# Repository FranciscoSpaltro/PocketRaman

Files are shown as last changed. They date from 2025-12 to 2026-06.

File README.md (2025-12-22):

# PocketRaman
Low-cost portable Raman spectrometer prototype developed at SUPSI. Based on Raspberry Pi 4 and STM32F469I-DISCO, using a TCD1304 linear CCD with ADC and DMA-based acquisition. Includes custom 3D-printed mechanical parts to reuse optical mounting components and reduce cost.

## Status

This project implements a first working pipeline for CCD readout using:
- Timer-driven ADC sampling with DMA
- UART DMA streaming to host
- Python-based real-time visualization

Data acquisition and transmission are functional.
Frame synchronization relative to ICG/SH is currently under refinement,
which may cause horizontal drift in the displayed signal.

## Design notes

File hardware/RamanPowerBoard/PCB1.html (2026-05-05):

Altium customize

# Board Information Report

Date: | | 5/5/2026
Time: | | 11:02:39
Elapsed Time: | | 00:00:00
Filename: | | C:\Users\francisco.spaltro\OneDrive - SUPSI\Desktop\PocketRaman\hardware\RamanPowerBoard\PCB1.PcbDoc

## Contents

Contents

Routing

Routing Information

## Routing

Routing Information
Routing completion | 100,00%
Connections | 118
Connections routed | 118
Connections remaining | 0

Back to top

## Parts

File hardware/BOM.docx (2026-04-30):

BOM – PCB A

QTY | NAME | DESCRIPTION | SEL
6 | STACKPOLE RMCF0805ZT0R00TR-ND | RESISTOR 0 OHM | SEL.000028 (4400 PZ)
3 | YAGEO 311-100CRTR-ND (RC0805FR-07100RL) | RESISTOR 100 OHM | SEL.000034 (4400 PZ)
1 | STACKPOLE RMCF0805FT150RTR-ND | RESISTOR 150 OHM | SEL.000038 (4400 PZ)
1 | YAGEO 311-220FRTR-ND (RC1206FR-07220RL) | RESISTOR 220 OHM | SEL.001229 (20 PZ)
3 | STACKPOLE RMCF0805FT1K00 | RESISTOR 1 KOHM | SEL.000049 (4400 PZ)
9 | YAGEO 311-10KARTR-ND (RC0805JR-0710KL) | RESISTOR 10 KOHM | SEL.000062 (4400 PZ)
2 | Kemet C0805C100J5GACTU | CAPACITOR 10 pF | SEL.000911 (984 PZ)
1 | Kemet C0805C101J5GACTU | CAPACITOR 100 pF | SEL.000857 (990 PZ)
19 | Kemet C0805C104K3RAC7800 | CAPACITOR 100 nF | SEL.000087 (1000 PZ)
4 | Samsung CL21B475KOFNNNE | CAPACITOR 4.7 uF | SEL.001701 (4 PZ)
1 | Yageo CC0805KKX7R7BB105 | CAPACITOR 1 uF | SEL.000086 (1000 PZ)
5 | Samsung CL21B106KOQNNNE | CAPACITOR 10 uF | SEL.000690 (29 PZ)
2 | Kyocera AVX F381A106MMA | CAPACITOR 10 uF | SEL.001502 (6 PZ)
1 | Kyocera AVX F951A226MPAAQ2 | CAPACITOR 22 uF | SEL.000755 (10 PZ)
2 | BAS40-7-F | DIODE | SEL.000247 (72 PZ)
1 | ONSEMI MBRA340T3G | DIODE SCHOTTKY 40V 3A SMA | SEL.001040 (16 PZ)
1 | ONSEMI BC846BLT1G | TRANS NPN 65V 0.1A SOT23-3 | SEL.001790 (21 PZ)
1 | DIOTEC BC857B-AQ | TRANS PNP 45V 0.1A SOT23-3 | SEL.000739 (8 PZ)
2 | MMZ1608B601CTAH0 | INDUCTOR; SMT (0603); FERRITE-BEAD; 600; TOL=+/-25%; 0.5A; -55 DEGC TO +125 DEGC | SEL.001136 (163 PZ)
1 | NCV1117ST33T3G | Linear Voltage Regulator IC Positive Fixed 1 Output 1A SOT-223 | SEL.000321 (5 PZ)
1 | NCV1117STAT3G | IC REG LINEAR POS ADJ 1A SOT-223 | NOT AVAILABLE
1 | CG04874-8M | 8 MHz ±20ppm Crystal 8pF 500 Ohms 2-SMD, No Lead | SEL.000471 (1 PZ)
1 | MCP6001UT-E/OT | Microchip MCP6001UT-E/OT Op Amp, 1MHz Rail-Rail, 1.8 - 6 V, 5-Pin SOT-23 | Microchip Technology Inc. MCP6001UT-E/OT | SEL.000435 (10 PZ)
1 | STM32F446RCT6TR | ARM® Cortex®-M4 STM32F4 Microcontroller IC 32-Bit Single-Core 180MHz 256KB (256K x 8) FLASH 64-LQFP (10x10) | SEL.001604 (1 PZ)
1 | LED-LTST-C190KRKT | Red 631nm LED Indication - Discrete 2V 0603 (1608 Metric) | SEL.000817 (254 PZ)
2 | OMRON SW1020TR-ND | Switch Tactile N.O. SPST Round Button Gull Wing 0.05A 12VDC 1.5N SMD Embossed T/R | SEL.000613 (21 PZ)
1 | MCP9808T-E/MC | TEMPERATURE SENSOR | -
1 | TCD1304DG8ZAW | LINEAR CCD DETECTOR | -
1 | AMPHENOL ICC (FCI)10118194-0001LF | Micro USB, Input Output Connectors, B TYPE RECEPTACLE with flange | SEL.000758 (47 PZ)
1 | USBLC6-4SC6 | VERY LOW CAPACITANCE ESD PROTECTION | SEL.000267 (25 PZ)
1 | SILICON LABS 336-1160-5-ND (CP2102-GM) | USB Bridge, USB to UART USB 2.0 UART Interface 28-QFN (5x5) | SEL.000346 (6 PZ)
3 | Generic 40 mils drill size, 100 mils step. TOTAL: 36 PIN | Pin header x3
1 | | Pin header x4
1 | | Pin header x5
3 | | Pin header x6
1 | HARWIN M20-7861546 | PIN SOCKET SMD 2x15 (CCD SENSOR) | NOT AVAILABLE
1 | PHOENIX 1706207 | TERM BLOCK HDR 2POS 2.54MM | NOT AVAILABLE
1 | PHOENIX 1821465 | TERM BLOCK HDR 9POS 2.54MM | NOT AVAILABLE

BOM – PCB B

QTY | NAME | DESCRIPTION | SEL
7 | STACKPOLE RMCF0805ZT0R00TR-ND | RESISTOR 0 OHM | SEL.000028 (4400 PZ)
1 | STACKPOLE RMCF0805FT10R0TR-ND | RESISTOR 10 OHM | SEL.000031 (4400 PZ)
6 | YAGEO 311-10KARTR-ND (RC0805JR-0710KL) | RESISTOR 10 KOHM | SEL.000062 (4400 PZ)
1 | Kemet C0805C101J5GACTU | CAPACITOR 100 pF | SEL.000857 (990 PZ)
7 | Kemet C0805C104K3RAC7800 | CAPACITOR 100 nF | SEL.000087 (1000 PZ)
1 | Taiyo Yuden 587-2994-2-ND (UMK316AB7475KL-T) | CAPACITOR 4.7 uF | SEL.000799 (500 PZ)
1 | Samsung 1276-1075-2-ND (CL31A106KAHNNNE) | CAPACITOR 10 uF | SEL.001145 (990 PZ)
4 | Panasonic PCE3836TR-ND (EEE-FK1V101XP) | CAPACITOR 100 uF | SEL.001144 (48 PZ)
1 | ONSEMI FSV15150V | DIODE SCHOTTKY 150V 15A TO2773 | SEL.000715 (6 PZ)
2 | AO 785-1106-2-ND (AOD417) | P-Channel 30V 25A, 2.5W Ta, 50W Tc Surface Mount TO-252, D-Pak | SEL.001625 (8 PZ)
1 | MICROCHIP TC4420COA713TR-ND | MOSFET Power Driver 6A,4.5 to 18V, Non-Inverting,8-Pin SOIC | Microchip Technology Inc. TC4420COA | SEL.001374 (1 PZ)
1 | WÜRTH 732-11711-ND (74437529203220) | FIXED IND 22UH 23.9A 4.9MOHM SMD | SEL.001103 (3 PZ)
2 | POLOLU A4988 | Stepper Motor Driver Carrier | -
1 | PHOENIX 1706207 | TERM BLOCK HDR 2POS 2.54MM | NOT AVAILABLE
1 | PHOENIX 1821465 | TERM BLOCK HDR 9POS 2.54MM | NOT AVAILABLE
2 | MOLEX WM11252-ND (436500402) | Connector Header Through Hole, Right Angle 4 position 0.118 (3.00mm) | SEL.001696 (3 PZ)
4/2 | PIN SOCKET | 1 x 8 POS / 2 x 8 POS

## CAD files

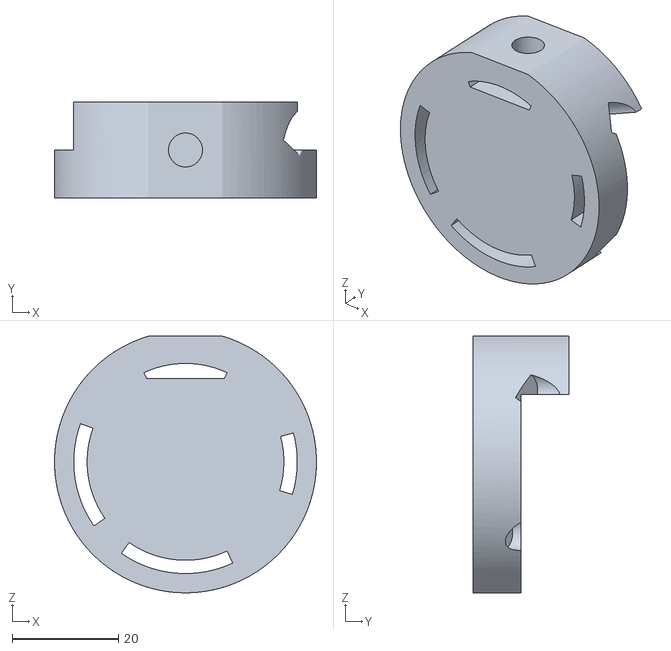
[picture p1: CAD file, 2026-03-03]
mechanical/13_grating-cage.stl
49.2 x 18.0 x 48.2

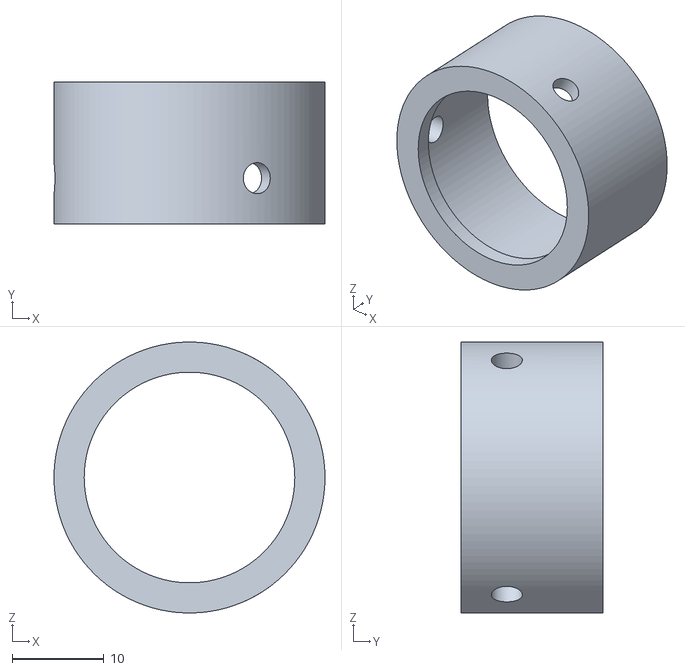
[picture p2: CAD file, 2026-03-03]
mechanical/11_25-4-lens-adapter.stl
29.6 x 15.5 x 29.6

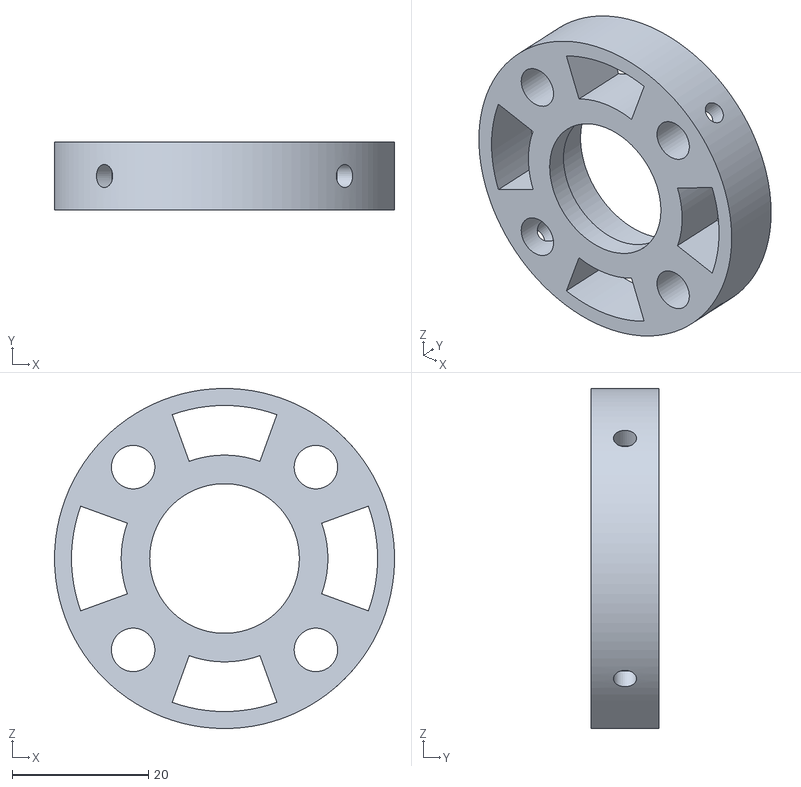
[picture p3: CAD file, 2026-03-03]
mechanical/06_filter-cage.stl
50.0 x 10.0 x 50.0

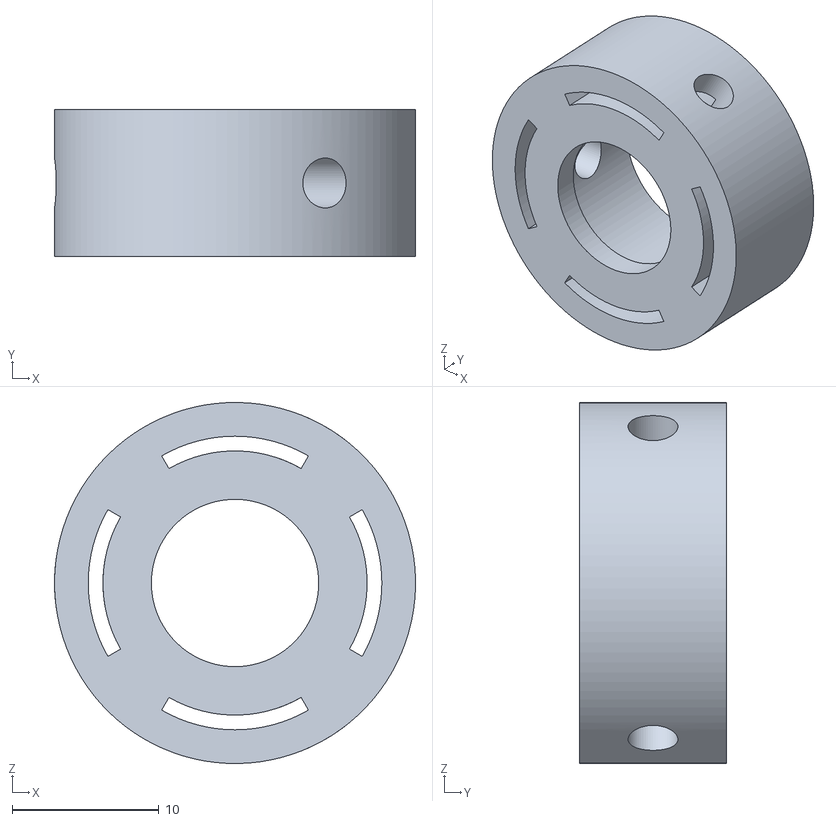
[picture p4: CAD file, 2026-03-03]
mechanical/02_12-7-lens-adapter-a.stl
24.6 x 10.0 x 24.6

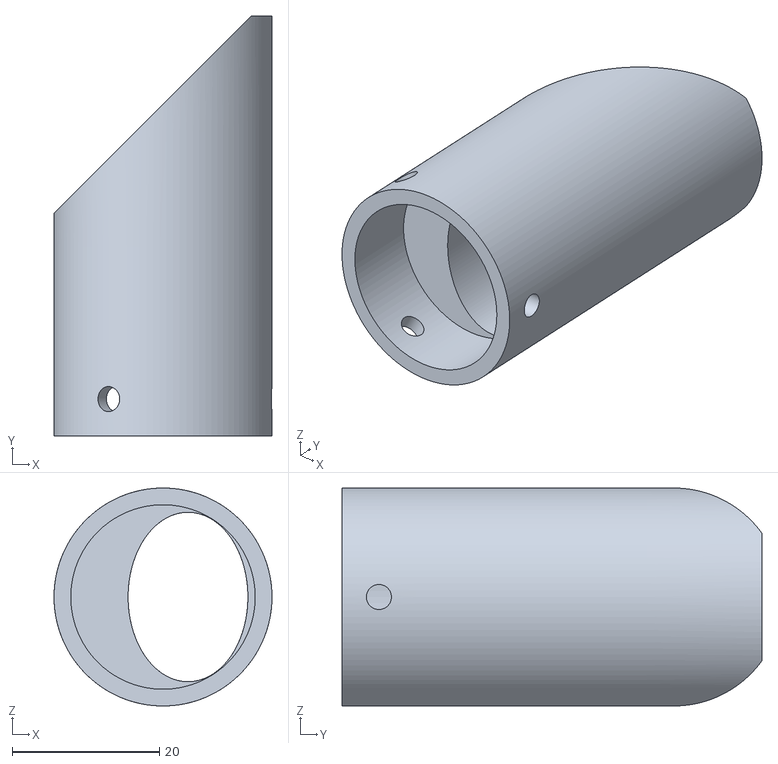
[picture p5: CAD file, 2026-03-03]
mechanical/04_dichroic-adapter.stl
29.6 x 57.0 x 29.6

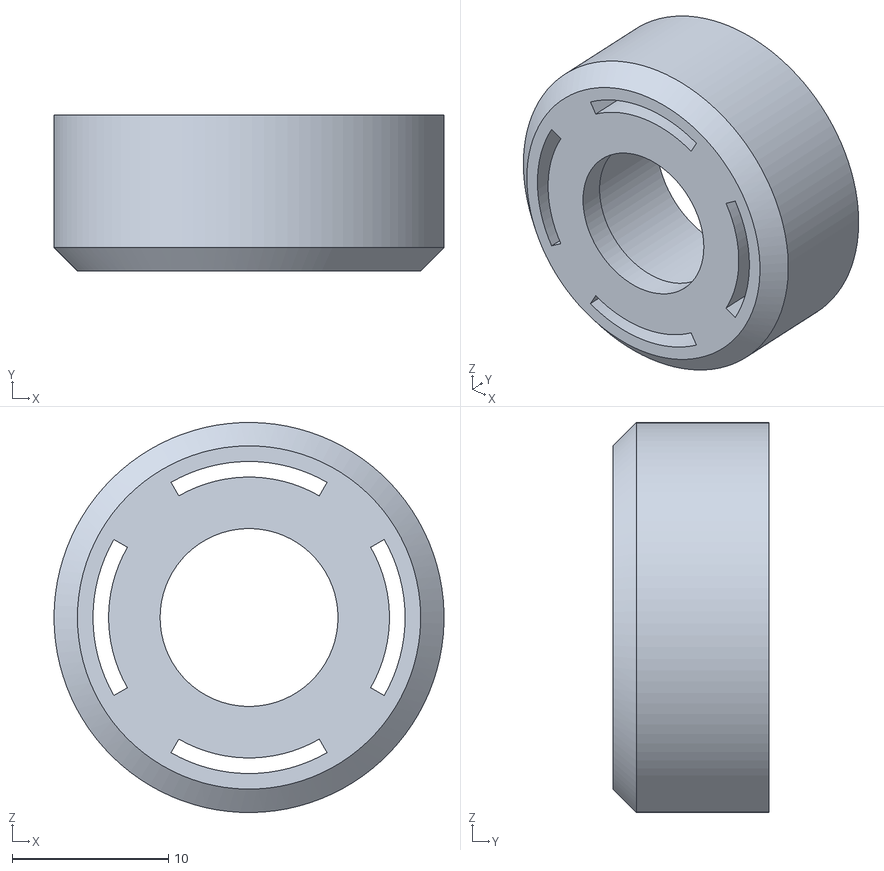
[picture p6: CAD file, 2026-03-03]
mechanical/08_12-7-lens-adapter-b.stl
25.0 x 10.0 x 25.0

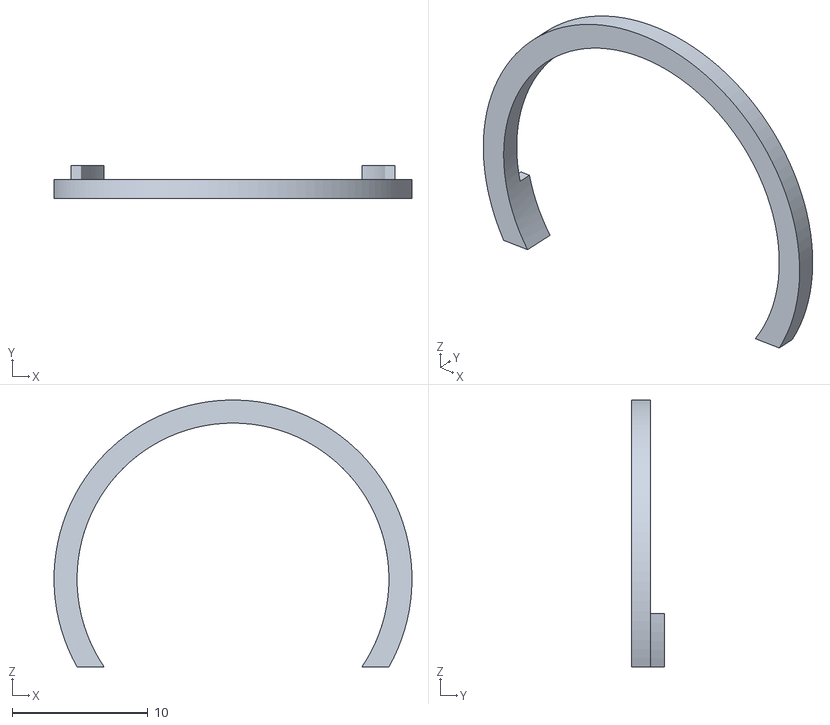
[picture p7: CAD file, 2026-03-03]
mechanical/05_dichroic-stop.stl
26.4 x 2.40 x 19.7

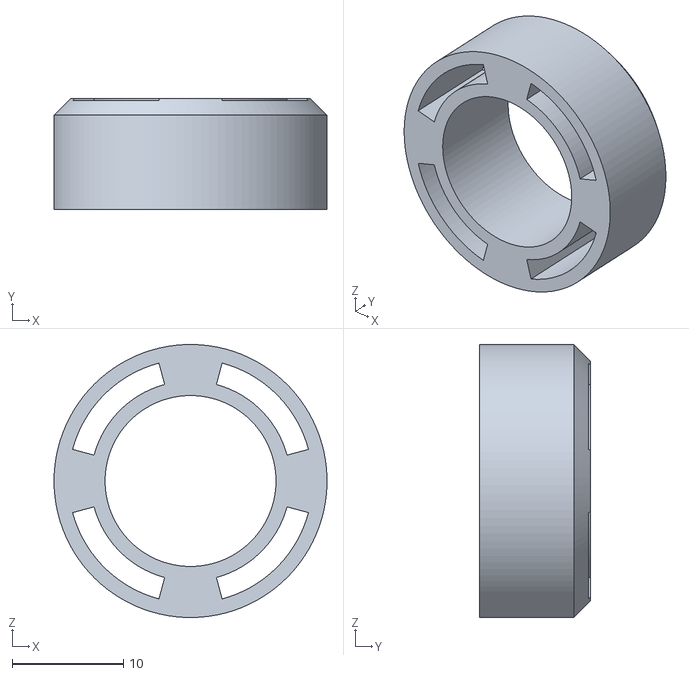
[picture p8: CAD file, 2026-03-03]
mechanical/01_laser-adapter.stl
24.6 x 10.0 x 24.6

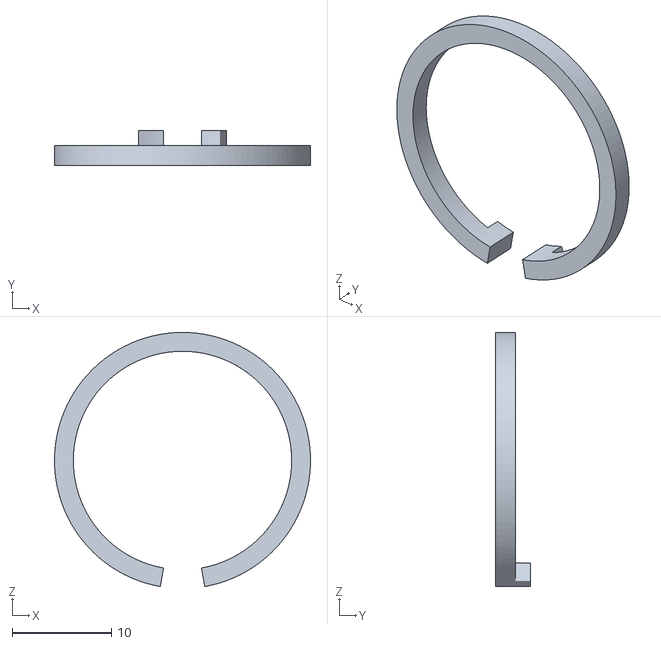
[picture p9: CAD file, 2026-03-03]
mechanical/07_filter-stop.stl
25.8 x 3.50 x 25.6

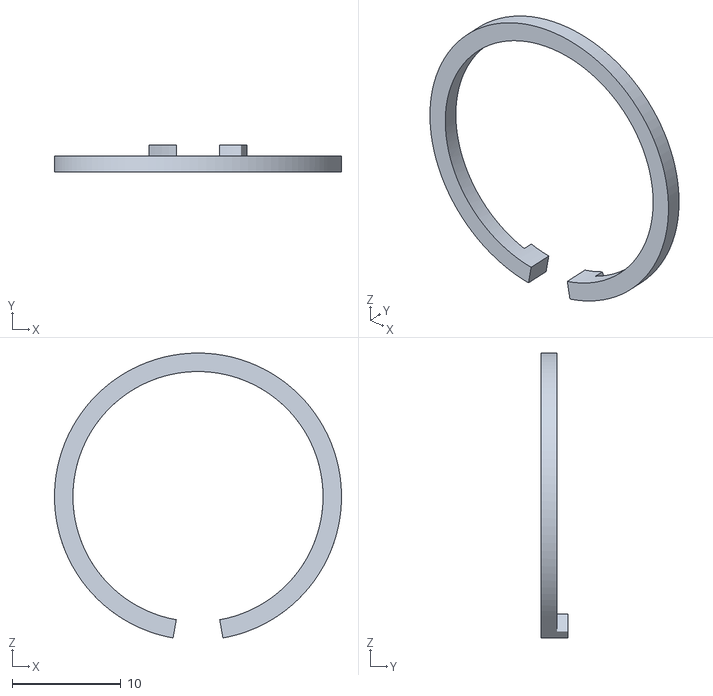
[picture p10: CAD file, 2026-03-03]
mechanical/12_25-4-lens-stop.stl
26.4 x 2.50 x 26.2

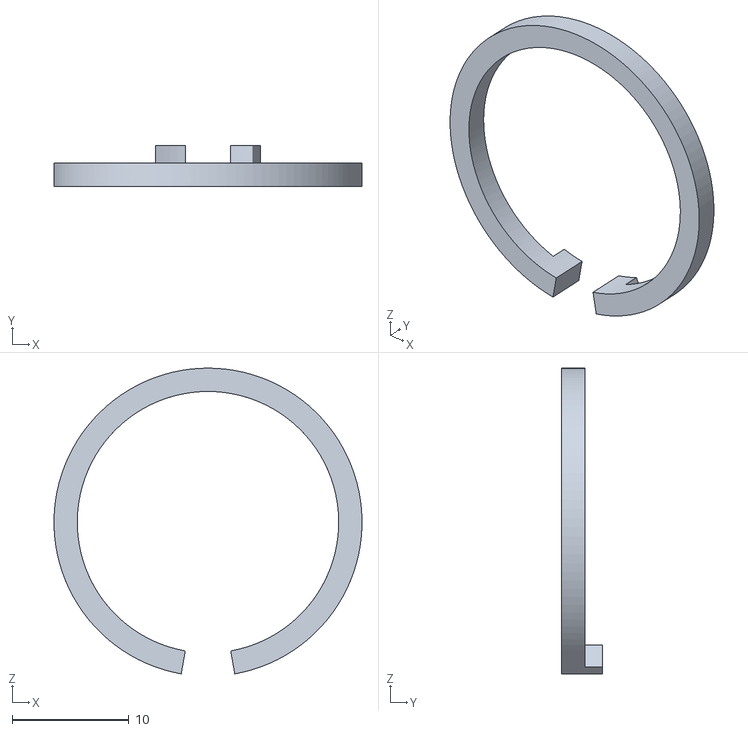
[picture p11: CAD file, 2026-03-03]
mechanical/10_slit-stop.stl
26.4 x 3.50 x 26.2

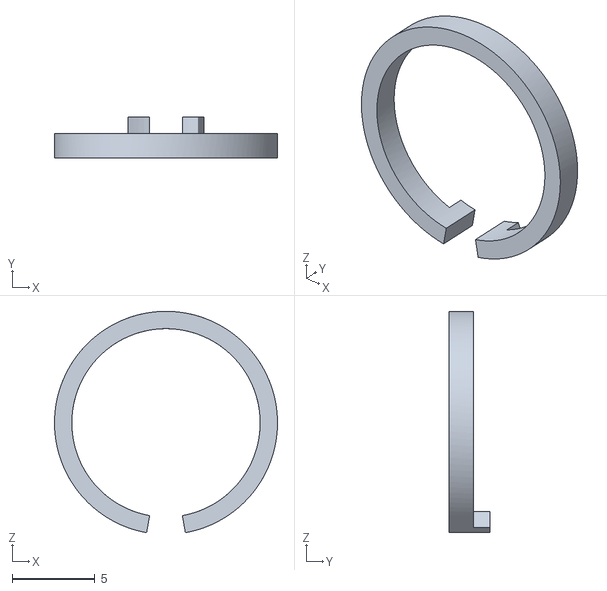
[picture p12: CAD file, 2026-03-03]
mechanical/03_12-7-lens-stop.stl
13.5 x 2.50 x 13.4

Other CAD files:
mechanical/09_slit-adapter.stl

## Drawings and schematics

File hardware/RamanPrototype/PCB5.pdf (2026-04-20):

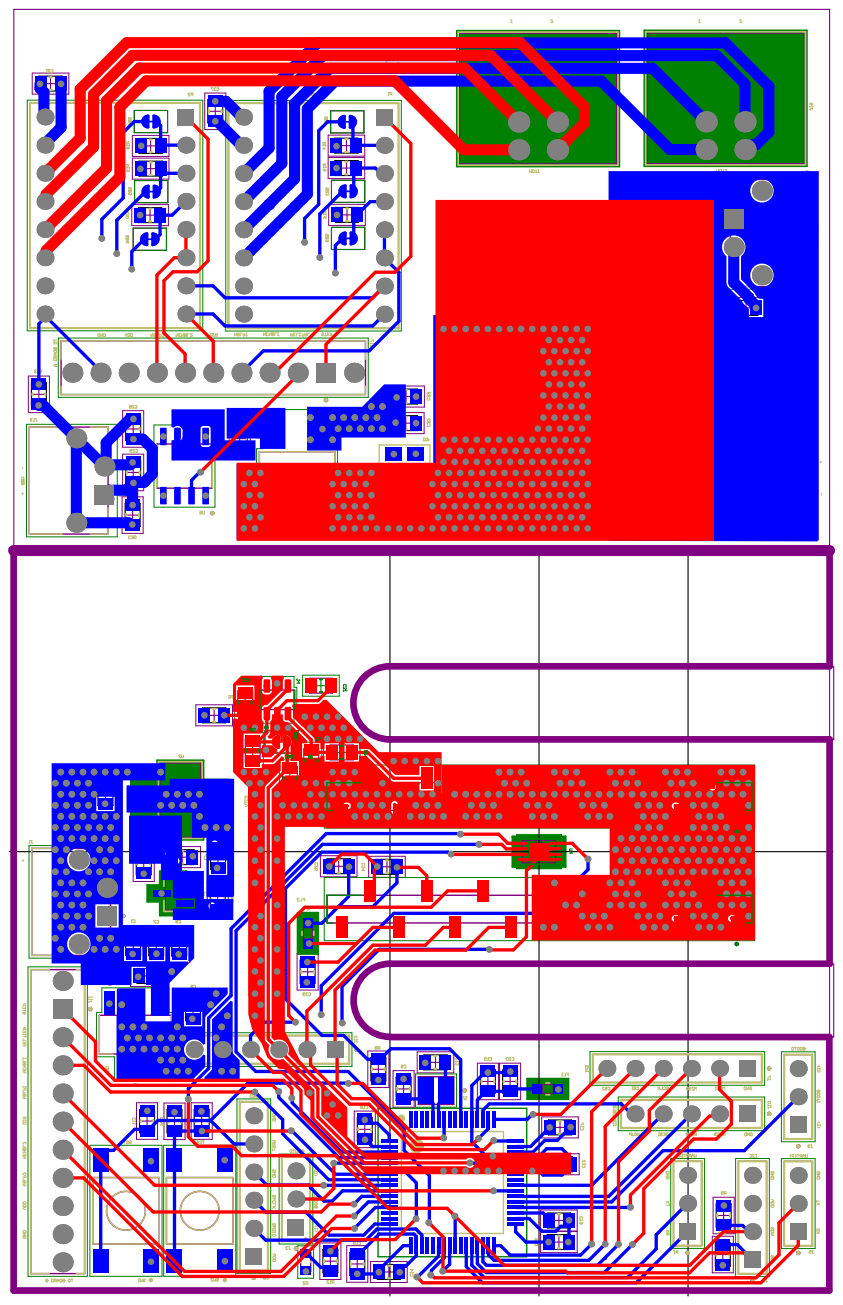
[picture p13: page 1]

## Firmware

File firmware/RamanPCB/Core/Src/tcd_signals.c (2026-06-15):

#include <tcd_signals.h>
#include <tcd_variables.h>

extern TIM_HandleTypeDef htim1;
extern TIM_HandleTypeDef htim3;
extern TIM_HandleTypeDef htim5;
extern ADC_HandleTypeDef hadc1;
extern volatile uint8_t send_now;
//extern volatile uint8_t is_flushing;
extern volatile uint32_t n_accum;
extern volatile uint32_t n_skip_counter;

volatile uint8_t adc_busy = 0;
volatile uint8_t can_save = 1;
volatile uint32_t skip_counter = 0;

volatile uint16_t adc_buffer[CCD_PIXELS];
volatile uint32_t accum_buffer[CCD_PIXELS] = {0};
volatile uint16_t frame[CCD_PIXELS];

volatile int n = 0;
volatile int real_SH_EDGES = 0;
uint32_t sh_ccr[SH_EDGES_MAX];
volatile int acumulaciones = 0;

const uint32_t TS0_tics = 1;
const uint32_t TS1_tics = 2;
const uint32_t TS2_tics = 10;

uint32_t TS3_tics = 0;
uint32_t TS4_tics = 0;
uint32_t TS5_tics = 0;
uint32_t TS6_tics = 0;


/**
 * @brief Calculo de los tiempos de cada etapa de la integración y de la cantidad de overhead necesaria para cumplir con el tiempo de lectura
 *
 * @param[in]	t_int_us	Nuevo tiempo de integración en microsegundos
 * @return		void
 *
 * @post Se configuraron los nuevos valores de TS3_tics, TS4_tics, TS5_tics, TS6_tics y n
 * Deben recalcularse las tablas CCR de SH e ICG
 */
void calculate_times(uint32_t t_int_us){
    // fM = 2 MHz -> 1 us = 2 tics
	const uint16_t tics_por_microsegundo = 2;			// [REVISAR] -> hacerlo portable
    uint32_t t_int_tics = 0;

    if(t_int_us < T_INT_MIN_US)
        t_int_tics = T_INT_MIN_US * tics_por_microsegundo;
    /*else if(t_int_us > T_INT_MAX_US)
    	t_int_tics = T_INT_MAX_US * tics_por_microsegundo;*/
    else
        t_int_tics = t_int_us * tics_por_microsegundo;

    /*
     * MODELO: desde el momento que baja ICG:
     * S0: desde la bajada de ICG hasta la subida de SH -> (100, 500, 1000) ns
     * S1: tiempo en ON de SH dentro del tiempo en OFF de ICG -> (1000, -, -) ns [si se necesita padding se puede modificar este -> hay que actualizar ICG]
     * S2: desde la bajada de SH hasta la subida de ICG -> (1000, 5000, - ) ns
     * S3: desde la subida de ICG hasta la subida de SH -> t_int - S1 - S2
     * S4: tiempo en ON de SH -> TS1 (sin padding)
     * S5: tiempo en OFF de SH -> t_int - S4
     * S6: desde la bajada de SH hasta la bajada de ICG -> TS5 - TS0
     */
    TS3_tics = t_int_tics - TS1_tics - TS2_tics;
    TS4_tics = TS1_tics;
    TS5_tics = t_int_tics - TS4_tics;
    TS6_tics = TS5_tics - TS0_tics;

    const uint32_t t_readout_tics = 7400 * tics_por_microsegundo;

    // Cálculo de 'n' (Número de pulsos de limpieza durante el readout)
    /*
     * TS3 + n * (TS4 + TS5) + TS4 + TS6 >= t_readout
     * n >= (t_readout - TS3 - TS4 - TS6) / (TS4 + TS5) = (t_readout - TS3 - TS4 - TS6) / t_int
     */

    uint32_t overhead = TS0_tics + TS1_tics + TS2_tics + TS3_tics + TS4_tics + TS6_tics;	// Tiempo sin contar los ciclos TS4-TS5

    if (t_readout_tics + t_int_tics > overhead) {
         n = (t_readout_tics - TS3_tics - TS4_tics - TS6_tics + t_int_tics - 1) / t_int_tics;
    } else {
         n = 0;
    }

}

/**
 * @brief Actualización de la tabla de valores CCR para SH
 *
 * @post Se actualizaron los valores del vector sh_ccr
 */
void build_SH_table(void)
{
	// Se arma un vector local con todos los tiempos en base al 'n' actualizado
	static uint32_t sh_dt[SH_EDGES_MAX];

	sh_dt[0] = TS0_tics;
	sh_dt[1] = TS1_tics;
	sh_dt[2] = TS2_tics + TS3_tics;

	for(int i = 0; i < n; i++){
		sh_dt[3 + 2 * i] = TS4_tics;
		sh_dt[3 + 2 * i + 1] = TS5_tics;
	}

	sh_dt[2 + 2 * n + 1] = TS4_tics;

	// De S0 a S0 hay 4 flancos (extremos de S1 y del último S4) más 2*n de cada S4 que se repite
	real_SH_EDGES = 4 + 2 * n;

    uint32_t t = 0;

    // Se arma el CCR (acumulativo)
    for (uint32_t i = 0; i < real_SH_EDGES; i++) {
        t += sh_dt[i];
        sh_ccr[i] = t;
    }

}


/**
 * @brief Inicia o detiene los timers 2, 3 y 4
 *
 * @param[in]	start	1 para iniciarse, 0 para detenerse
 *
 * @return		void
 *
 * @post Se invierte el estado de funcionamiento de los canales y timers que correspondan, cargando los vectores de CCR via DMA en caso de ser necesario
 */
void start_timers(uint8_t start){
	if(start == 1){
		__HAL_TIM_SET_COUNTER(&htim1, 0);
		__HAL_TIM_SET_COUNTER(&htim3, 0);
		__HAL_TIM_SET_COUNTER(&htim5, 0);

		__HAL_TIM_SET_AUTORELOAD(&htim5, sh_ccr[real_SH_EDGES-1] + TS6_tics);
		__HAL_TIM_SET_COMPARE(&htim5, TIM_CHANNEL_2, sh_ccr[0]);

		HAL_TIM_PWM_Start_IT(&htim1, TIM_CHANNEL_1);
		HAL_TIM_OC_Start_DMA(&htim5, TIM_CHANNEL_2, (uint32_t*)sh_ccr, real_SH_EDGES);
		HAL_TIM_PWM_Start_IT(&htim5, TIM_CHANNEL_4);
		HAL_TIM_PWM_Start(&htim3, TIM_CHANNEL_3);

		HAL_TIM_Base_Start(&htim1);
		HAL_TIM_Base_Start(&htim5);
		HAL_TIM_Base_Start(&htim3);
	} else if(start == 0){
		HAL_TIM_PWM_Stop(&htim3, TIM_CHANNEL_3);
		HAL_TIM_PWM_Stop(&htim1, TIM_CHANNEL_1);
		HAL_TIM_OC_Stop_DMA(&htim5, TIM_CHANNEL_2);
		HAL_TIM_PWM_Stop_IT(&htim5, TIM_CHANNEL_4);
		HAL_TIM_PWM_Stop_IT(&htim1, TIM_CHANNEL_1);

		HAL_TIM_Base_Stop(&htim3);
		HAL_TIM_Base_Stop(&htim1);
		HAL_TIM_Base_Stop(&htim5);
	}

}


/**
 * @brief  Callback del Timer (Output Compare).
 * Sincroniza el inicio del ADC con la señal ICG (Integration Clear Gate) del CCD.
 *
 * @post	Si los recursos estaban permitidos, se activó el DMA-ADC
 */
void HAL_TIM_PWM_PulseFinishedCallback(TIM_HandleTypeDef *htim) {
	if(htim->Instance == TIM5 && htim->Channel == HAL_TIM_ACTIVE_CHANNEL_4){
		//if(is_flushing == 1)
			//return;

		if(skip_counter < n_skip_counter){
			skip_counter++;
			return;
		} else {
			skip_counter = 0;
		}

		if(adc_busy == 1 || can_save == 0)
			return;

		adc_busy = 1;
		HAL_ADC_Start_DMA(&hadc1, (uint32_t*)adc_buffer, CCD_PIXELS);
	}
}

/**
 * @brief  Callback de finalización de conversión ADC (DMA).
 * Se ejecuta cuando el buffer de píxeles del CCD se ha llenado.
 *
 * @post	Se detuvo el DMA-ADC y se liberó adc_busy. Se liberó el semáforo, se activó send_now (envío de datos)
 * y se intercambiaron los buffers.
 */
void HAL_ADC_ConvCpltCallback(ADC_HandleTypeDef* hadc) {
    if (hadc->Instance == ADC1) {
    	if(n_accum == 1){
    		for (int i = 0; i < CCD_PIXELS; i++) {
				frame[i] = (uint16_t)(adc_buffer[i]);
			}

			adc_busy = 0;
			can_save = 0;
			send_now = 1;
			return;
    	}

    	for(int i = 0; i < CCD_PIXELS; i++){
    		accum_buffer[i] += adc_buffer[i];
    	}

    	acumulaciones++;

    	if(acumulaciones >= n_accum){
			for (int i = 0; i < CCD_PIXELS; i++) {
				frame[i] = (uint16_t)(accum_buffer[i] / n_accum);
				accum_buffer[i] = 0;
			}

			acumulaciones = 0;
    		adc_busy = 0;
    		can_save = 0;
    		send_now = 1;

    	}

    	else{
    		adc_busy = 0;
    		can_save = 1;
    		send_now = 0;
    	}
    }
}

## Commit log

2025-12-22 WIP: frame sync via ICG + twin timer (OC-based), ADC aligned but frame length not final
2025-12-22 Implement CCD timing sync: ICG, fM, and ADC phase-locked (v1)
    - TIM2 configured as ICG (frame timing)
    - TIM3 configured as fM (pixel clock)
    - TIM4 configured as ADC trigger, phase-locked to fM
    - TIM5 configured as SH (period), triggered by ICG
    ADC sampling time set to 28 cycles to reduce step artifacts.
    This is a first functional version; further tuning is expected.
2026-01-13 Refactor CCD timing generation using TIM2 OC + DMA
    Major architectural change to generate SH and ICG signals using TIM2 in Output Compare Toggle mode driven by DMA. This replaces manual control to ensure precise, jitter-free timing.
    Key changes:
    - Implemented TIM2 + DMA circular buffer logic for signal generation.
    - Added `START_OFFSET` to prevent race conditions at t=0 and ensure SH/ICG synchronization.
    - Implemented `calculate_times` and `build_SH_table` to dynamically calculate the number of cleaning pulses (n) based on integration time using integer math.
    - Switched to static "worst-case" buffer allocation (MAX_EDGES) to avoid dynamic memory usage.
    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
2026-01-13 Feat: Implement synchronized fM (TIM3) with phase-lock padding
    Implemented Master Clock (fM) generation and synchronized it with the Control Signals (SH/ICG) to ensure deterministic timing.
    Key Changes:
    - Master-Slave Configuration: Configured TIM2 (SH/ICG) as Master and TIM3 (fM) as Slave in Trigger Mode. Both timers now start on the exact same clock cycle, eliminating startup jitter.
    - Phase Alignment (t_4 datasheet =0): Updated START_OFFSET to 22 ticks. This aligns the ICG rising edge precisely with the fM falling edge.
    - Dynamic Phase Locking: Implemented a padding algorithm in calculate_times:
    - Calculates the remainder of the total frame duration relative to the fM period (45 tick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
2026-01-13 feat: Implement CCD capture with 4x oversampling and visualization fix
    STM32 Firmware:
    - Configured TIM3 for master clock (fM) generation.
    - Implemented ADC control triggered on the ICG rising edge (TIM2 Callback).
    - Enabled NVIC interrupts for ADC1 (Stream 0) and UART6 (Stream 6).
    - Implemented buffer with fixed synchronization Header (0x4652, 0x414E...).
    - Enabled UART transmission at 460800 baud with 4x oversampling.
    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
2026-01-14 Esta version es tecnicamente incorrecta pero funciona, por eso la guardo
2026-01-14 Implementation of prescaler by overrun and remove 1/4 frames to stabilize
2026-01-19 fix: dynamic integration time and frame noise
    - Fixed logic in `setup_timer_icg_sh` and main loop to ensure correct signal polarity and counter reset when changing integration time.
    - Added `END_BUFFER` to valid frames to filter out incomplete transmissions (noise).
2026-01-28 start: pcb for tcd and output stage, mounting design for soft grip
    [TCD1304.kicad_pcb, TCD1304.kicad_sch]
2026-01-29 pcb prototype
    [TCD1304.kicad_pcb]
2026-01-30 add Altium project (start)
    [Componentes.SchLib, IC.PcbLib, IC.SchLib, PCB1.PcbDoc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]
2026-02-09 backup before converting sch into hierarchical design
    [Componentes.PcbLib, Componentes.SchLib, IC.PcbLib, IC.SchLib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]
2026-02-11 update hierarchical sheet PCB and complete circuit
    [Componentes.PcbLib, Componentes.SchLib, PCB1.PcbDoc, RamanPrototype.PrjPcb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]
2026-02-17 update SCHEMATICS - added a4988 support and general redesign
    [CI.PcbLib, CI.SchLib, CompAct.PcbLib, CompAct.SchLib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]
2026-02-17 starting PCB placement
    [CI.PcbLib, CI.SchLib, CompAct.PcbLib, CompPas.PcbLib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]
2026-03-03 complete first version of PCB - without protection diodes in LDO
    [01_laser-adapter.stl, 02_12-7-lens-adapter-a.stl, 03_12-7-lens-stop.stl, 04_dichroic-adapter.stl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]
2026-03-05 voltage devisor + buffer as TCD output signal
    [CI.SchLib, Components.PcbLib, Components.SchLib, Microcontroller.SchDoc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]
2026-03-05 separation of motor-peltier drivers
    [Components.PcbLib, Components.SchLib, Driver.SchDoc, Microcontroller.SchDoc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]
2026-03-06 redesign pcb, split motor stage and logic stage in two complementary pcbs
    [Components.PcbLib, Components.SchLib, Driver.SchDoc, Motor_PeltierDrivers.PrjPcb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]
2026-03-17 update pcb, change trigger adc from tim4 to tim1
    [CI.PcbLib, CI.SchLib, Components.PcbLib, Components.SchLib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]
2026-03-17 new version TCD template created for testing the new pin distribution
2026-03-27 PCB v4, separate boards + polygons; firmware adapted to migrate to STM32f446
    [Components.PcbLib, Components.SchLib, Main.SchDoc, Microcontroller.SchDoc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]
2026-04-01 Create PCB5 with new AGND path around OS
    [Components.PcbLib, Components.SchLib, Microcontroller.SchDoc, Sensor.SchDoc]
2026-04-20 PCB: correct vias, add multiple power vias, add gnd background, add snubber for peltier
    [Components.SchLib, Main.SchDoc, Microcontroller.SchDoc, Out.SchDoc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]
2026-04-27 split of pcb a-b; update routing; addition of real caps; rev version 1
    [CI.PcbLib, CI.SchLib, CompAct.PcbLib, CompAct.SchLib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]
2026-04-27 minimal changes in capacitors sch
    [Microcontroller.SchDoc, Out.SchDoc, PCB1.PcbDoc, Power.SchDoc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]
2026-04-28 modified with Andrea's initial corrections
    [PCB1.PcbDoc]
2026-04-28 final corrections before Daniele's review
    [CompAct.PcbLib, CompPas.PcbLib, PCB1.GBL, PCB1.GBO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]
2026-04-30 final details before quote; add BOM
    [Components.SchLib, Microcontroller.SchDoc, Out.SchDoc, PCB1.PcbDoc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]
2026-04-30 PCB B ready, PCB A needs minimal corrections (EUROCIRCUITS)
    [CI.PcbLib, PCB1.GBL, PCB1.GBO, PCB1.GBP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]
2026-05-04 final changes of PCB CHECKER (EUROCIRCUITS).- Production version 1.0
    [PCB7.GBL, PCB7.GBO, PCB7.GBP, PCB7.GBS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]
2026-05-04 Last version with the updates that are in the EuroCircuit cart
    [PCB1.GBL, PCB1.GBO, PCB1.GBP, PCB1.GBS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]
2026-05-05 added some capacitors on the PCB B - final version
    [Out.SchDoc, PCB1.GBL, PCB1.GBO, PCB1.GBP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]
